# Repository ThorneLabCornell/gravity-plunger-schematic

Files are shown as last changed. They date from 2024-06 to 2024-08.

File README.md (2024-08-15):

# gravity-plunger-schematic

Schematic created with Altium Designer

# BOM
| Item                                                      | Link                                                                                                                                                                                       | Quantity | Unit Price (USD) | Sub-Total (USD) |
| --------------------------------------------------------- | ------------------------------------------------------------------------------------------------------------------------------------------------------------------------------------------ | -------- | ---------------- | --------------- |
| Steel Support Rod 1"x3'                                   | [https://www.mcmaster.com/6061K65/](https://www.mcmaster.com/6061K65/)                                                                                                                     | 1        | 44.71            | 44.71           |
| Face Mount Shaft Collar 1"                                | [https://www.mcmaster.com/9677T2/](https://www.mcmaster.com/9677T2/)                                                                                                                       | 3        | 15.83            | 47.49           |
| Face Mount Shaft Collar 5/8"                              | [https://www.mcmaster.com/9677T23/](https://www.mcmaster.com/9677T23/)                                                                                                                     | 3        | 14.5             | 43.5            |
| Flange-Mounted Shaft Support 1"                           | [https://www.mcmaster.com/57745K23/](https://www.mcmaster.com/57745K23/)                                                                                                                   | 1        | 73.46            | 73.46           |
| Linear Bearing 5/8"                                       | [https://www.mcmaster.com/60595K74/](https://www.mcmaster.com/60595K74/)                                                                                                                   | 2        | 27.33            | 54.66           |
| External Retaining Ring 1 1/8"                            | [https://www.mcmaster.com/9968K25/](https://www.mcmaster.com/9968K25/)                                                                                                                     | 4        | 2.23             | 8.92            |
| Tight-Tolerance 2024 Aluminum Rod 5/8"x3'                 | [https://www.mcmaster.com/9061K17-9061K173/](https://www.mcmaster.com/9061K17-9061K173/)                                                                                                   | 1        | 64.99            | 64.99           |
| Multipurpose 6061 Aluminum, 3/16"x3'                      | [https://www.mcmaster.com/8974K21/](https://www.mcmaster.com/8974K21/)                                                                                                                     | 1        | 4.27             | 4.27            |
| 10-24 Thread Size, 1-1/2" Long, Fully Threaded (25 Units) | [https://www.mcmaster.com/90044A115/](https://www.mcmaster.com/90044A115/)                                                                                                                 | 1        | 12.36            | 12.36           |
| 1/4"-20 Thread Size, 3/4" Long Screws (50 Units)          | [https://www.mcmaster.com/91251A540/](https://www.mcmaster.com/91251A540/)                                                                                                                 | 1        | 11.38            | 11.38           |
| 10-24 Thread Size, 7/16" Long Screws (25 Units)           | [https://www.mcmaster.com/91864A090/](https://www.mcmaster.com/91864A090/)                                                                                                                 | 1        | 10.19            | 10.19           |
| M3 x 0.5 mm Thread, 16 mm Long Screws (100 Units)         | [https://www.mcmaster.com/92005A126/](https://www.mcmaster.com/92005A126/)                                                                                                                 | 1        | 4.73             | 4.73            |
| M3 x 0.5 mm Thread Nuts (100 Units)                       | [https://www.mcmaster.com/90592A085/](https://www.mcmaster.com/90592A085/)                                                                                                                 | 1        | 2.62             | 2.62            |
| Air Tool Lubricant                                        | [https://www.amazon.com/Super-Lube-12004-Lubricant-Translucent/dp/B00N77RY8O](https://www.amazon.com/Super-Lube-12004-Lubricant-Translucent/dp/B00N77RY8O)                                 | 1        | 6.72             | 6.72            |
| DS3218MG Servo                                            | [https://www.amazon.com/ANNIMOS-Digital-Waterproof-DS3218MG-Control/dp/B076CNKQX4](https://www.amazon.com/ANNIMOS-Digital-Waterproof-DS3218MG-Control/dp/B076CNKQX4)                       | 1        | 13.59            | 13.59           |
| Shock Absorber                                            | [https://www.amazon.com/Bansbach-Easylift-FPD-1030A2-CW-Absorbers-Dampers/dp/B01IWIO3K4](https://www.amazon.com/Bansbach-Easylift-FPD-1030A2-CW-Absorbers-Dampers/dp/B01IWIO3K4)           | 1        | 10.33            | 10.33           |
| Arduino Uno R3                                            | [https://www.amazon.com/Arduino-A000066-ARDUINO-UNO-R3/dp/B008GRTSV6](https://www.amazon.com/Arduino-A000066-ARDUINO-UNO-R3/dp/B008GRTSV6)                                                 | 1        | 29               | 29              |
| Liquid Crystal LCD Screen                                 | [https://www.amazon.com/GeeekPi-Character-Backlight-Raspberry-Electrical/dp/B07S7PJYM6](https://www.amazon.com/GeeekPi-Character-Backlight-Raspberry-Electrical/dp/B07S7PJYM6)             | 1        | 10.99            | 10.99           |
| Electronic Grade Conformal Coating                        | [https://www.amazon.com/Clear-Electronic-Grade-Silicone-Squeeze/dp/B0063U2RT8](https://www.amazon.com/Clear-Electronic-Grade-Silicone-Squeeze/dp/B0063U2RT8)                               | 1        | 11.95            | 11.95           |
| M2M Jumper Wire Kit                                       | [https://www.amazon.com/Elegoo-EL-CP-004-Multicolored-Breadboard-arduino/dp/B01EV70C78](https://www.amazon.com/Elegoo-EL-CP-004-Multicolored-Breadboard-arduino/dp/B01EV70C78)             | 1        | 7                | 7               |
| Board Jumper Wire Kit                                     | [https://www.amazon.com/AUSTOR-Lengths-Assorted-Preformed-Breadboard/dp/B07CJYSL2T](https://www.amazon.com/AUSTOR-Lengths-Assorted-Preformed-Breadboard/dp/B07CJYSL2T)                     | 1        | 11.99            | 11.99           |
| Wire Connector Kit                                        | [https://www.amazon.com/Twidec-Connectors-Disconnect-Insulated-Assortment/dp/B09QWZ2V2G](https://www.amazon.com/Twidec-Connectors-Disconnect-Insulated-Assortment/dp/B09QWZ2V2G)           | 1        | 6.99             | 6.99            |
| Barrel Jack Connector                                     | [https://www.amazon.com/DZS-Elec-Connector-Experimental-5-5x2-1mm/dp/B07FDS11ZY](https://www.amazon.com/DZS-Elec-Connector-Experimental-5-5x2-1mm/dp/B07FDS11ZY)                           | 1        | 6.99             | 6.99            |
| Meter Stick                                               | https://www.amazon.com/Fisima-Large-Stainless-Measure-Straight/dp/B0C7Q3TKZH/                                                                                                              | 1        | 19.99            | 19.99           |
| 0.33uF Capacitor                                          | [https://www.digikey.com/en/products/detail/kemet/C412C334M5U5TA7200/818264](https://www.digikey.com/en/products/detail/kemet/C412C334M5U5TA7200/818264)                                   | 1        | 0.29             | 0.29            |
| 0.1uF Capacitor                                           | [https://www.digikey.com/en/products/detail/murata-electronics/RDER71H104K0K1H03B/4770969](https://www.digikey.com/en/products/detail/murata-electronics/RDER71H104K0K1H03B/4770969)       | 1        | 0.46             | 0.46            |
| 5V Voltage Regulator                                      | [https://www.digikey.com/en/products/detail/stmicroelectronics/L7805CV/585964](https://www.digikey.com/en/products/detail/stmicroelectronics/L7805CV/585964)                               | 1        | 0.58             | 0.58            |
| 12V Power Supply                                          | [https://www.digikey.com/en/products/detail/mean-well-usa-inc/RS-25-12/7706175](https://www.digikey.com/en/products/detail/mean-well-usa-inc/RS-25-12/7706175)                             | 1        | 11.93            | 11.93           |
| Circuit Protoboard                                        | [https://www.digikey.com/en/products/detail/sparkfun-electronics/PRT-12070/5230951](https://www.digikey.com/en/products/detail/sparkfun-electronics/PRT-12070/5230951)                     | 1        | 5.5              | 5.5             |
| 4 Pin Wire to Board Terminal                              | [https://www.digikey.com/en/products/detail/on-shore-technology-inc/OSTVN04A150/1588864](https://www.digikey.com/en/products/detail/on-shore-technology-inc/OSTVN04A150/1588864)           | 4        | 1.64             | 6.56            |
| 5 Pin Wire to Board Terminal                              | [https://www.digikey.com/en/products/detail/on-shore-technology-inc/OSTVN05A150/1588865](https://www.digikey.com/en/products/detail/on-shore-technology-inc/OSTVN05A150/1588865)           | 1        | 1.75             | 1.75            |
| 3 Pin Header                                              | [https://www.digikey.com/en/products/detail/samtec-inc/TS-103-G-A/1105459](https://www.digikey.com/en/products/detail/samtec-inc/TS-103-G-A/1105459)                                       | 1        | 1.19             | 1.19            |
| 200 Ohm Resistor                                          | [https://www.digikey.com/en/products/detail/stackpole-electronics-inc/CF14JT200R/1741336](https://www.digikey.com/en/products/detail/stackpole-electronics-inc/CF14JT200R/1741336)         | 2        | 0.1              | 0.2             |
| 10k Ohm Resistor                                          | [https://www.digikey.com/en/products/detail/stackpole-electronics-inc/CF14JT10K0/1741265](https://www.digikey.com/en/products/detail/stackpole-electronics-inc/CF14JT10K0/1741265)         | 3        | 0.1              | 0.3             |
| NO Push Button                                            | [https://www.digikey.com/en/products/detail/e-switch/PS1023ABLK/82862](https://www.digikey.com/en/products/detail/e-switch/PS1023ABLK/82862)                                               | 2        | 2.01             | 4.02            |
| Photoreflective Sensor                                    | [https://www.digikey.com/en/products/detail/tt-electronics-optek-technology/OPB704WZ/1637047](https://www.digikey.com/en/products/detail/tt-electronics-optek-technology/OPB704WZ/1637047) | 2        | 5.07             | 10.14           |
| 500mA Fuse                                                | [https://www.digikey.com/en/products/detail/eaton-electronics-division/BK-AGC-1-2-R/954156](https://www.digikey.com/en/products/detail/eaton-electronics-division/BK-AGC-1-2-R/954156)     | 1        | 0.83             | 0.83            |
| Fuse Holder Panel Mount                                   | [https://www.digikey.com/en/products/detail/littelfuse-inc/03453LF4HX040/16628034](https://www.digikey.com/en/products/detail/littelfuse-inc/03453LF4HX040/16628034)                       | 1        | 3.05             | 3.05            |
| Power Cord                                                | [https://www.digikey.com/en/products/detail/qualtek/311007-01/183390](https://www.digikey.com/en/products/detail/qualtek/311007-01/183390)                                                 | 1        | 3.37             | 3.37            |
| 20 AWG Red Wire 1'                                        | [https://www.digikey.com/en/products/detail/cnc-tech/1015-20-1-2000-004-1-TS/17799202](https://www.digikey.com/en/products/detail/cnc-tech/1015-20-1-2000-004-1-TS/17799202)               | 6        | 0.21             | 1.26            |
| 20 AWG Black Wire 1'                                      | [https://www.digikey.com/en/products/detail/cnc-tech/1015-20-1-2000-001-1-TS/17799212](https://www.digikey.com/en/products/detail/cnc-tech/1015-20-1-2000-001-1-TS/17799212)               | 6        | 0.204            | 1.22            |
| USB-A to USB-B M2M Wire                                   | [https://www.digikey.com/en/products/detail/assmann-wsw-components/AK672-2-2/947492](https://www.digikey.com/en/products/detail/assmann-wsw-components/AK672-2-2/947492)                   | 1        | 2.8              | 2.8             |

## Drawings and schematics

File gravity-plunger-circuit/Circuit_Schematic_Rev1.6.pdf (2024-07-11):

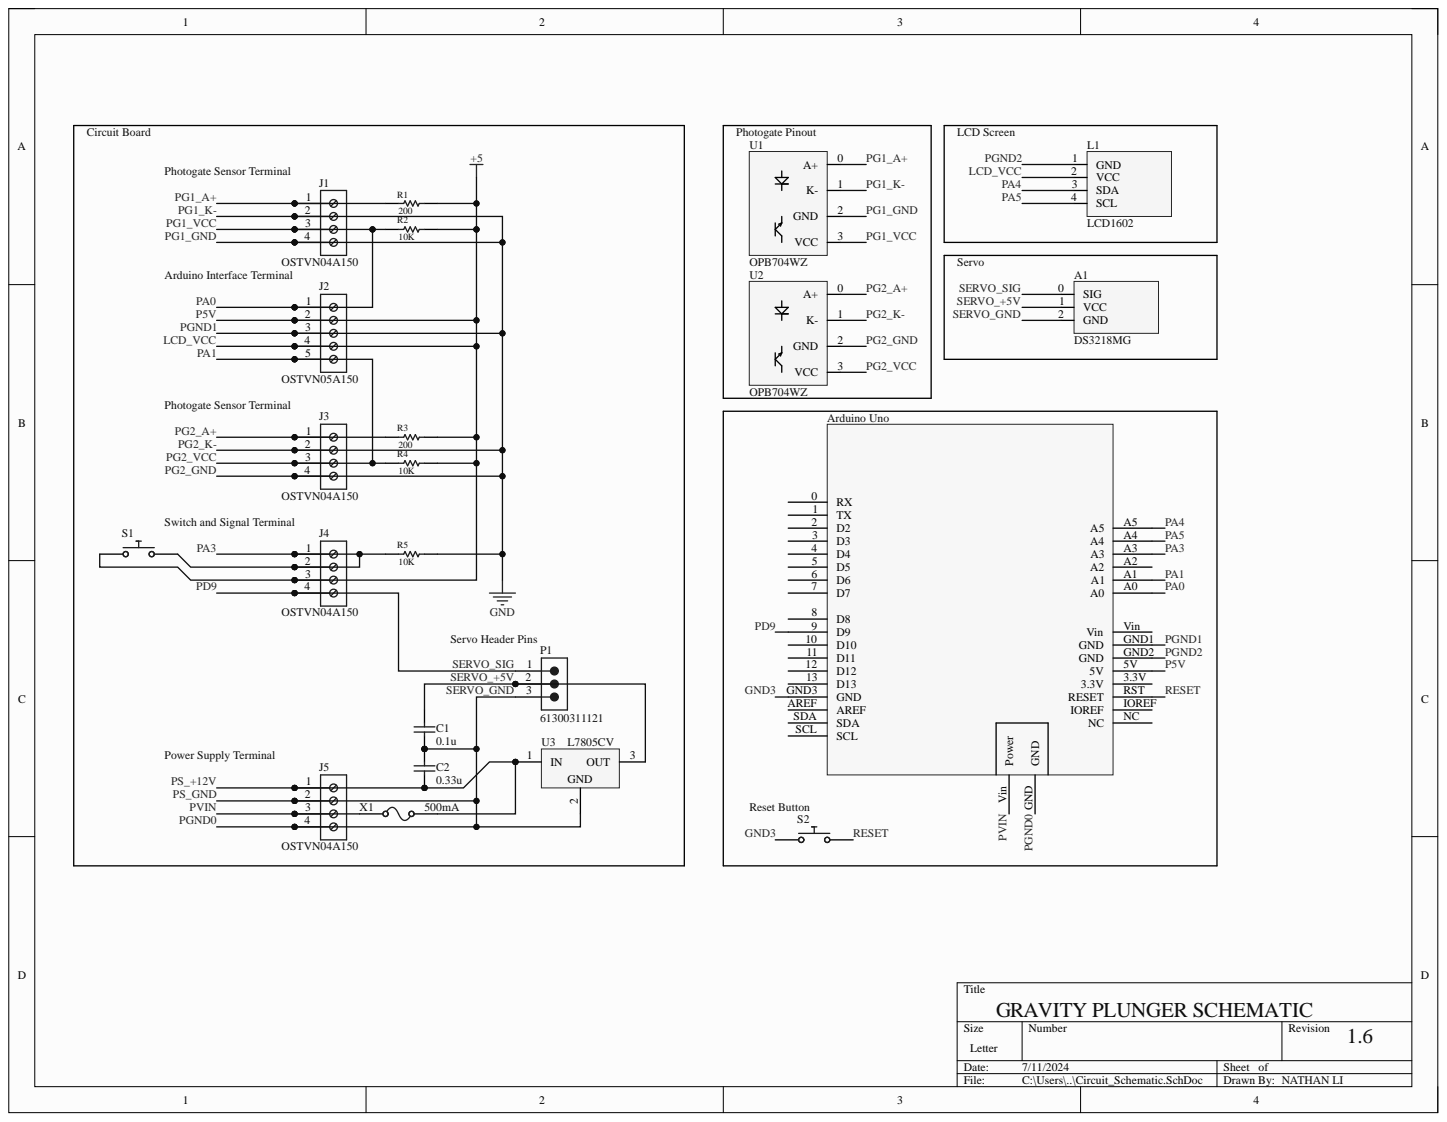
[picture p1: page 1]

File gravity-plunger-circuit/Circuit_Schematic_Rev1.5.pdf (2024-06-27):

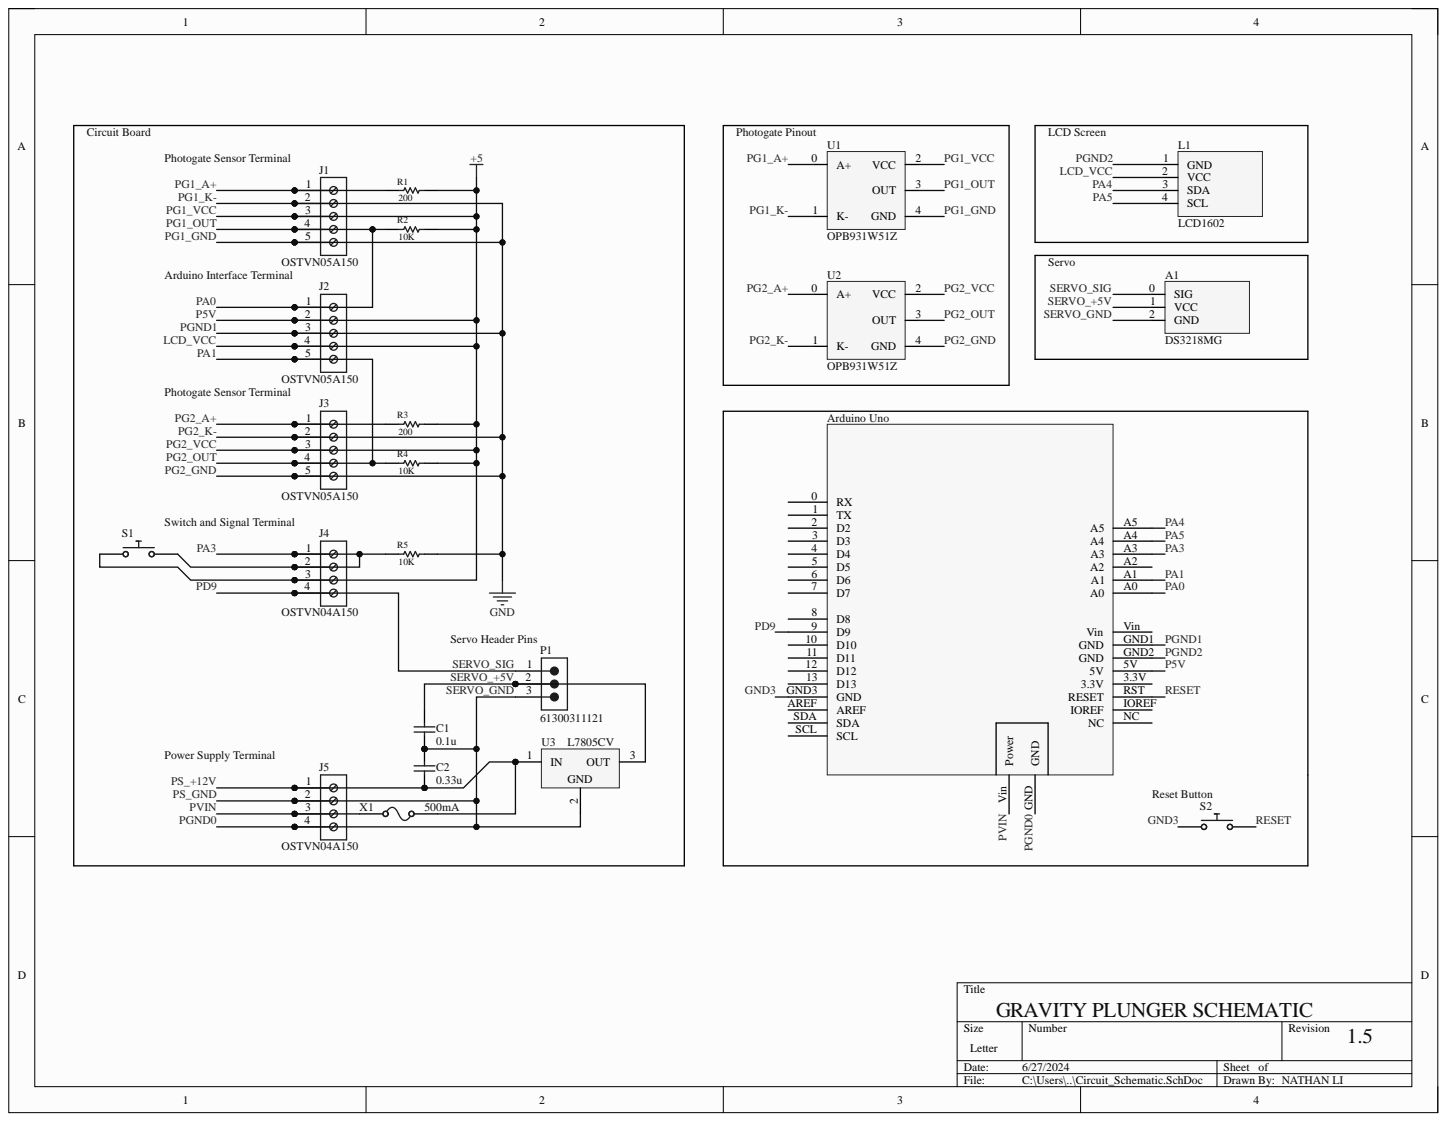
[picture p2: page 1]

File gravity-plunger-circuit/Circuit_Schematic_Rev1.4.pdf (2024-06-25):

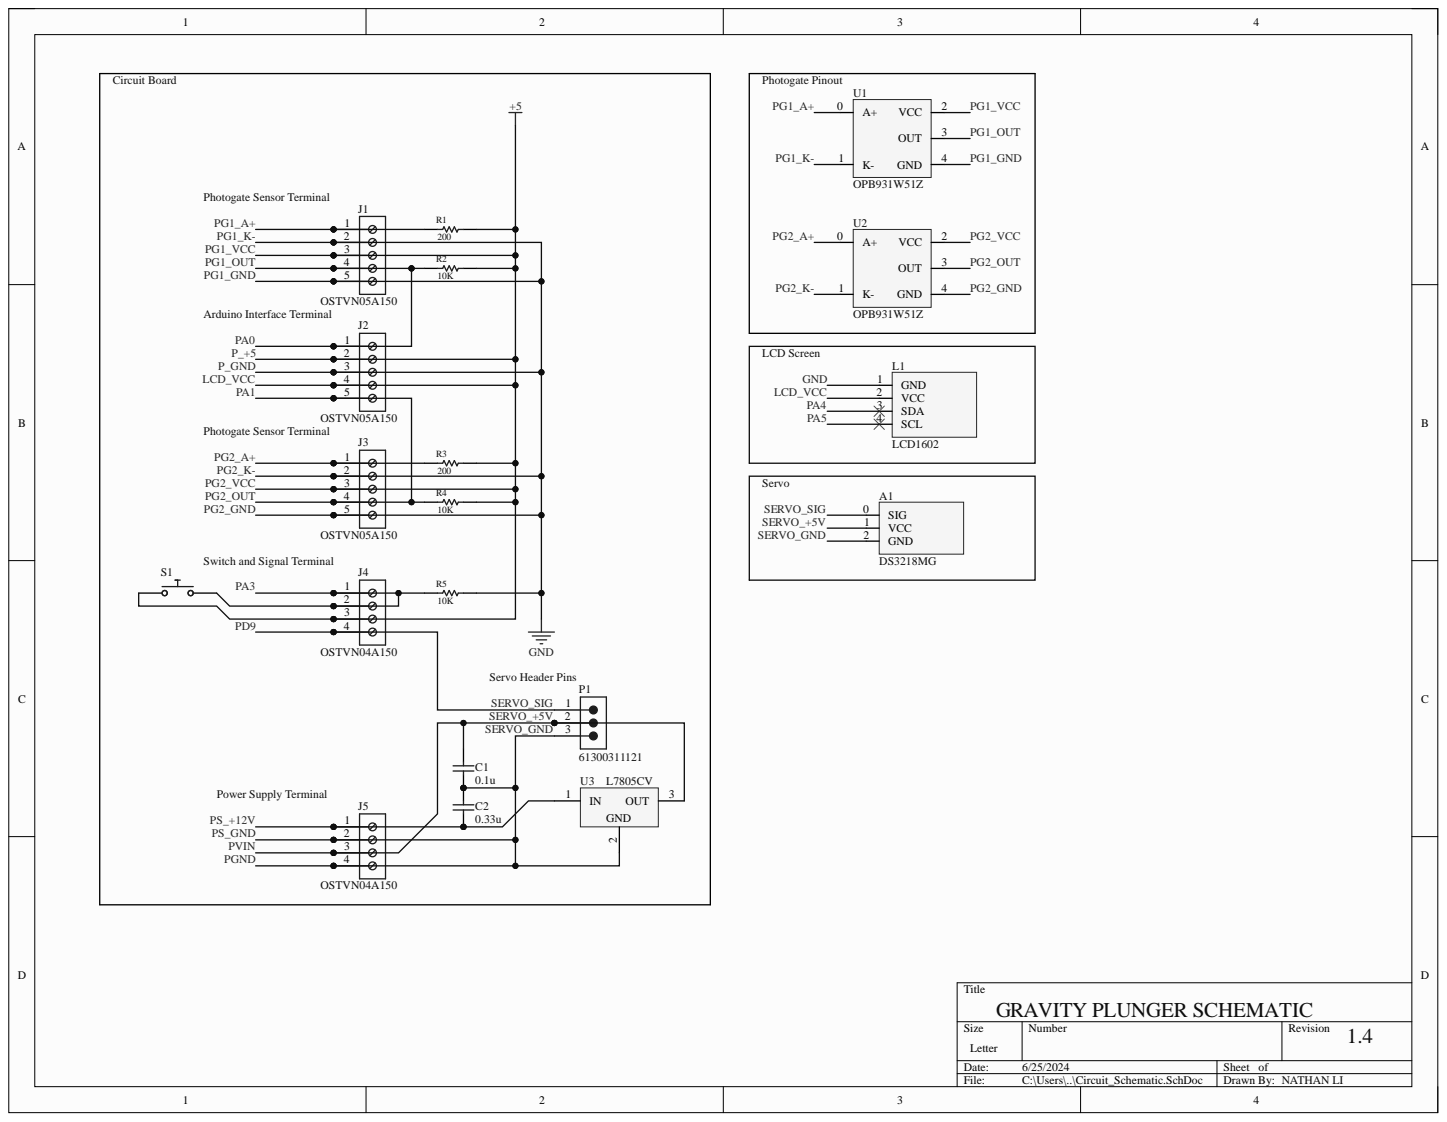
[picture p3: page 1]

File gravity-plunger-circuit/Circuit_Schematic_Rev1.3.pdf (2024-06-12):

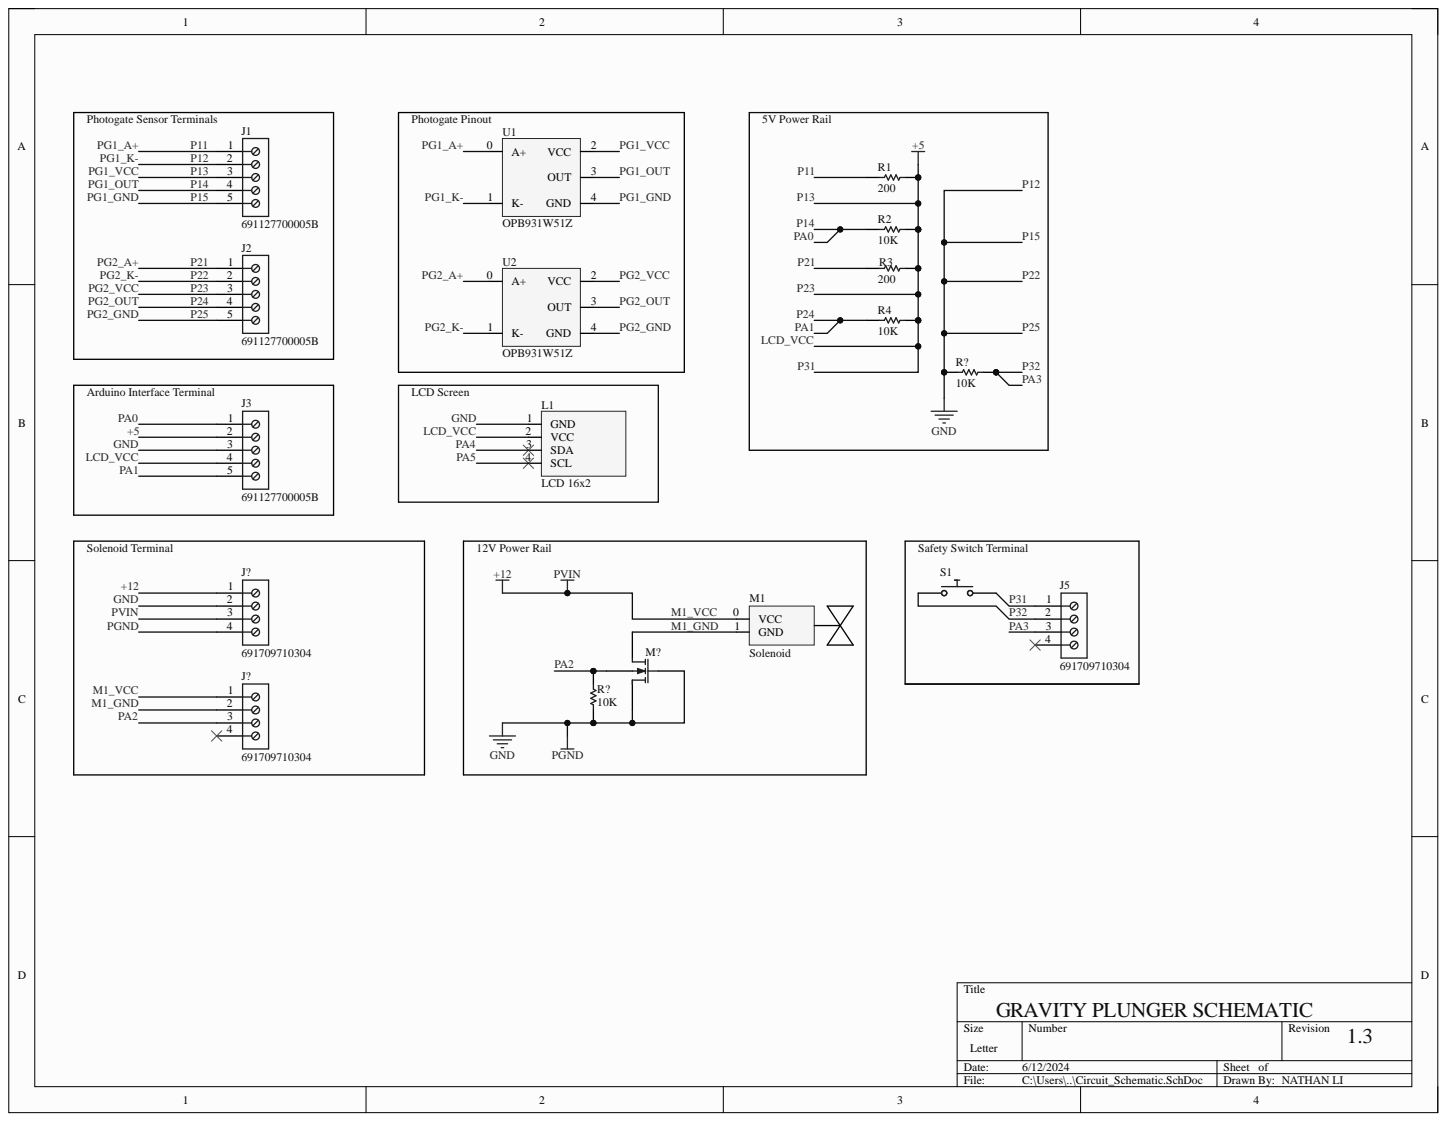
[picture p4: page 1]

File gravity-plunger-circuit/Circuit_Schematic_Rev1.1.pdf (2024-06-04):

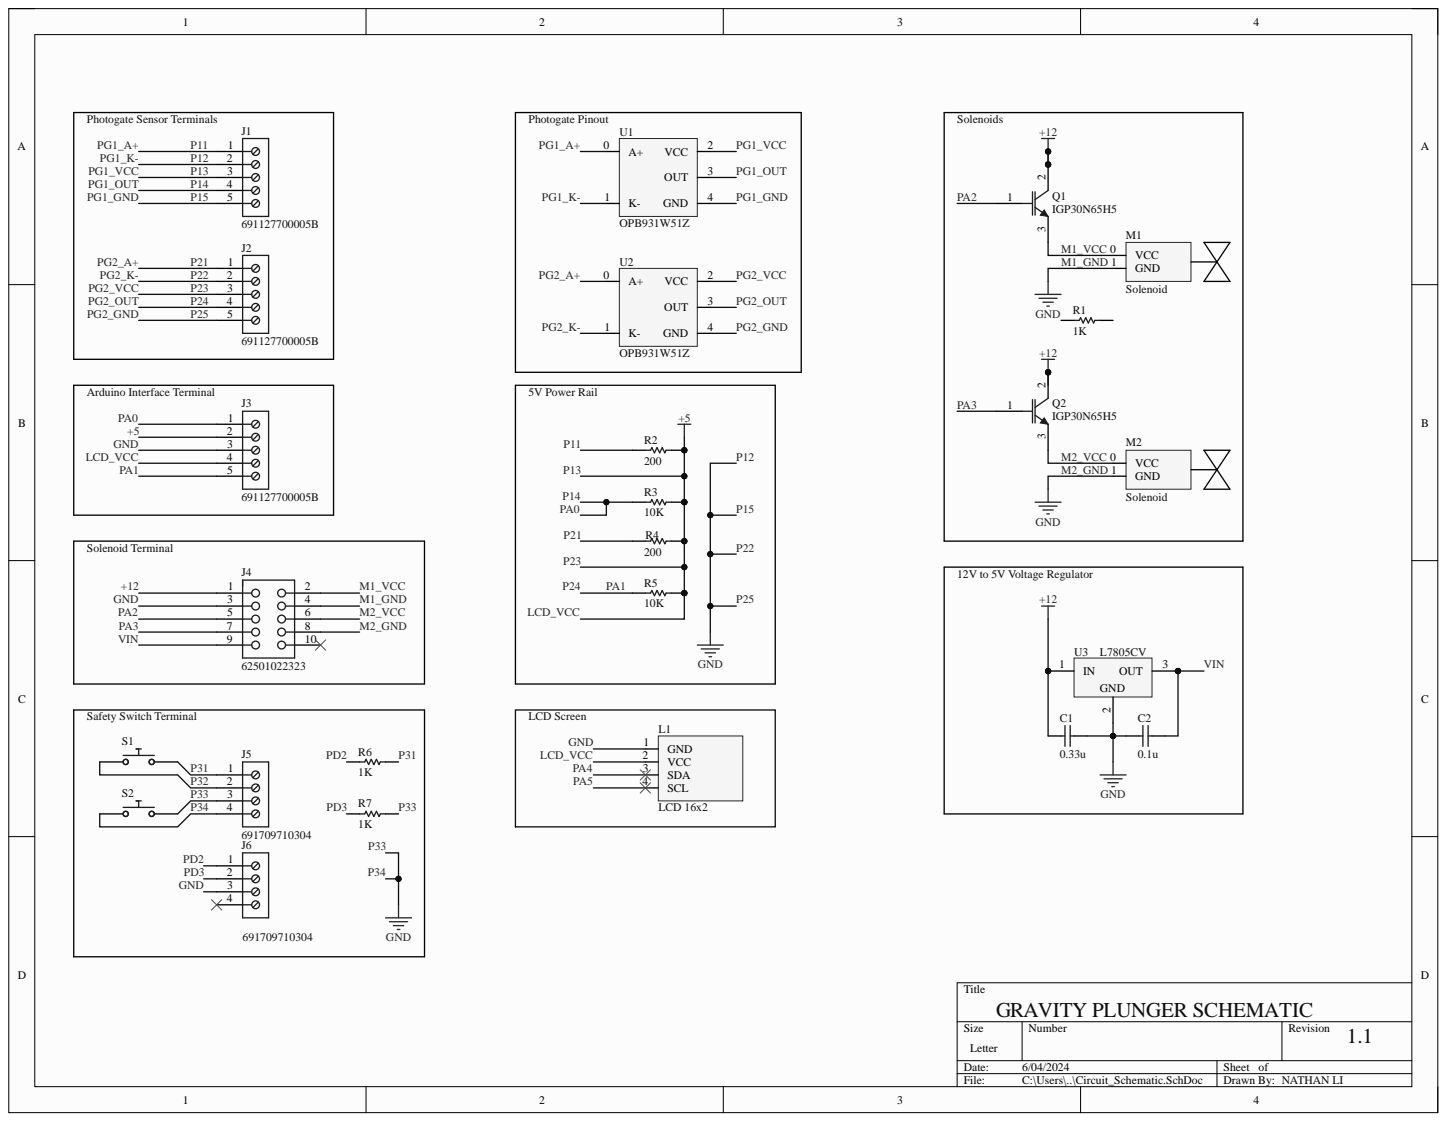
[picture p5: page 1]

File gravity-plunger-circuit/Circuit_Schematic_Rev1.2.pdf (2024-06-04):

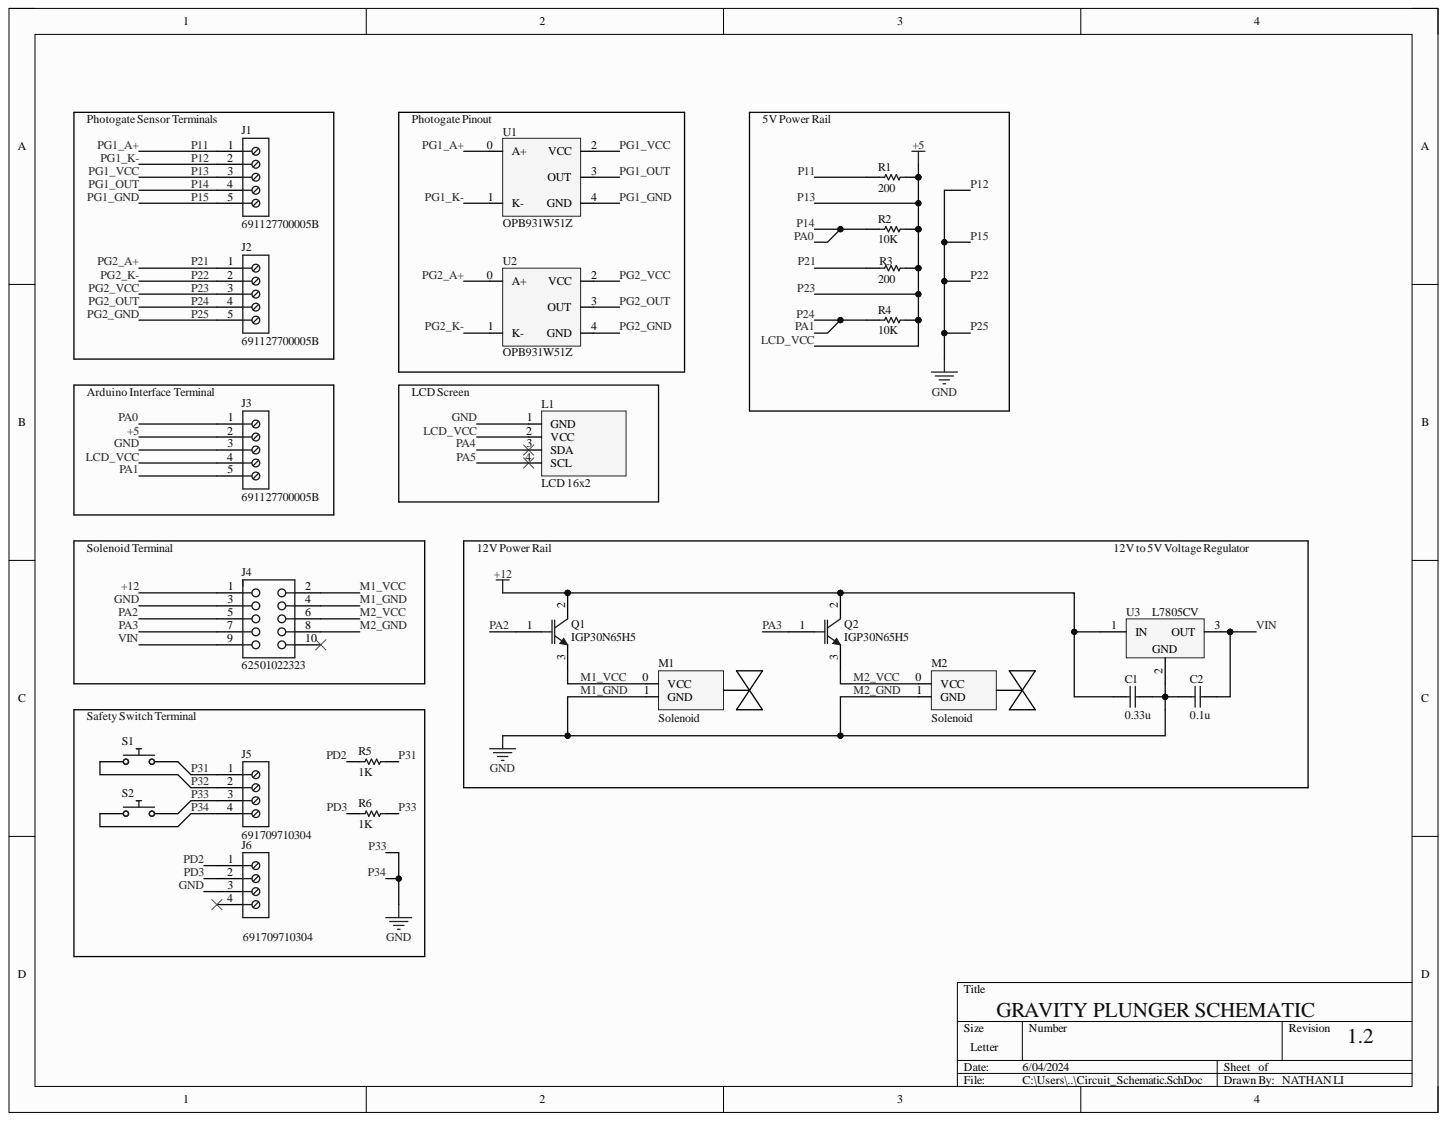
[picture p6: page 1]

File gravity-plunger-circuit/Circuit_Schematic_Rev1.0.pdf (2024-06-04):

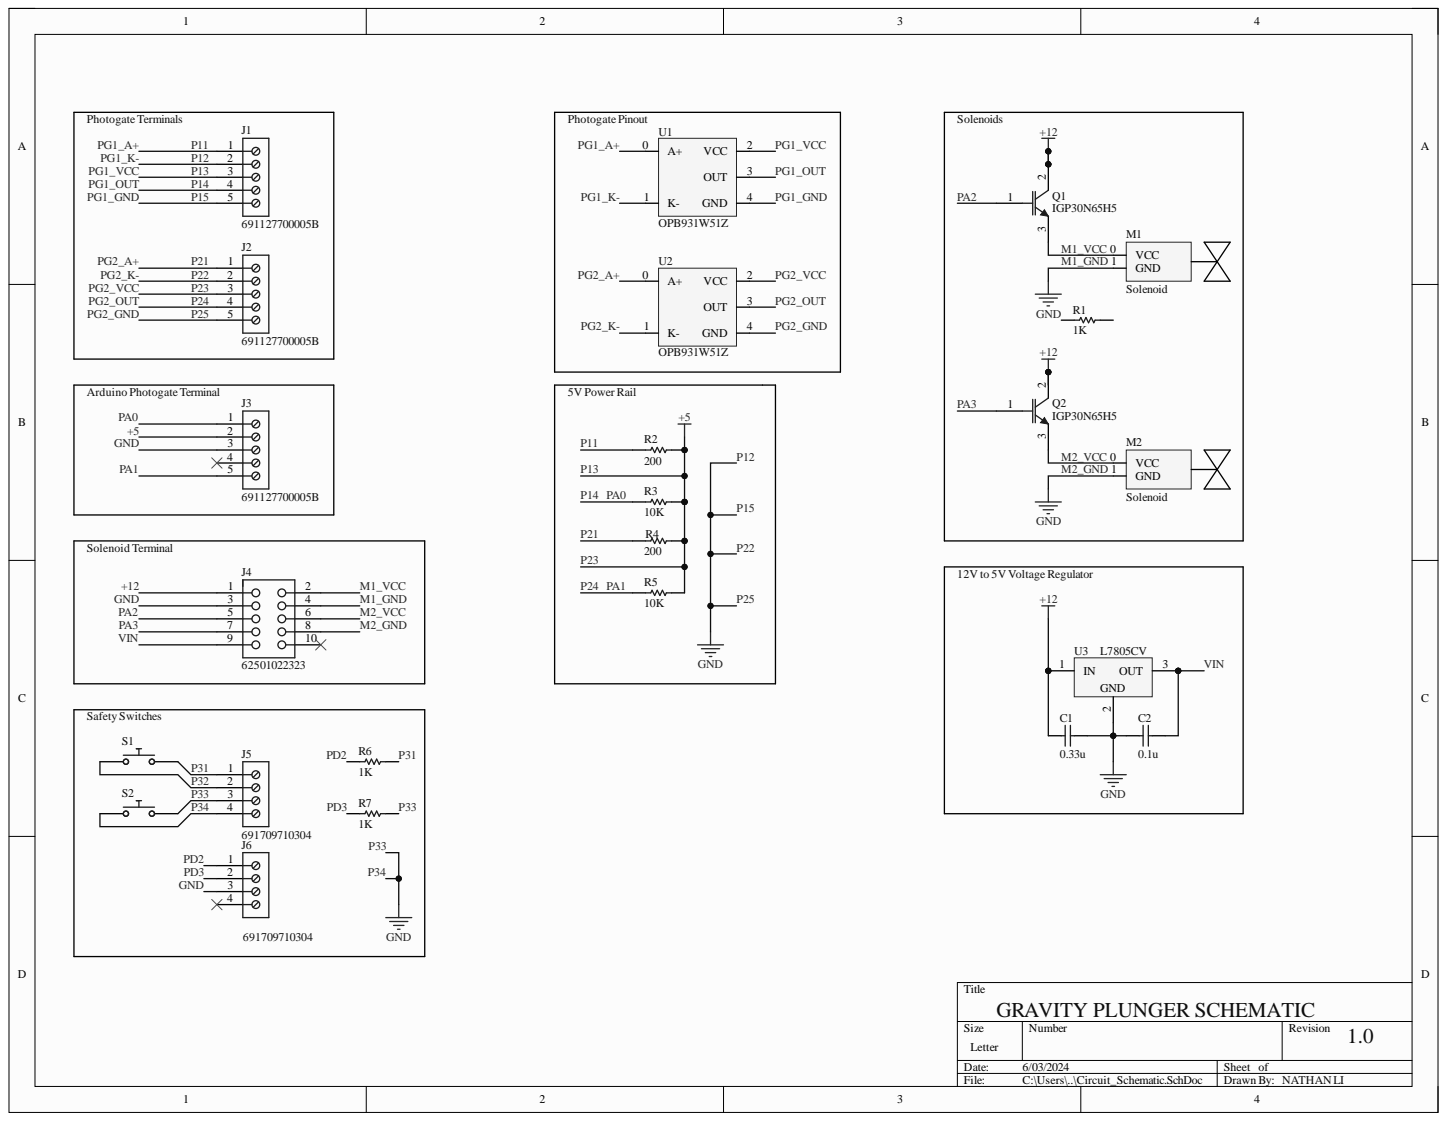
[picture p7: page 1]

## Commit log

2024-06-03 Added solenoid and voltage regulator schematics Created solenoid symbol Added terminal block schematics for photogates Added power rail schematics for photogates
    [Circuit_Schematic.SchDoc, SchemLib.SchLib, gravity-plunger-circuit.PrjPcb]
2024-06-03 + solenoid symbol + solenoid power schematic + 12V to 5V voltage regulator schematic + Net labels for photogate interrupters + Wire to board terminal schematics + Photogate power rail schematic
2024-06-03 Revision 1 + Switch and terminal schematic + Solenoid and +12V terminal schematic + Annotations and refactoring net labels
    [Circuit_Schematic.SchDoc]
2024-06-03 Added boxes and names to circuits
    [Circuit_Schematic.SchDoc]
2024-06-04 Rev 1.1 + LCD screen schematic
    [Circuit_Schematic.SchDoc, SchemLib.SchLib, gravity-plunger-circuit.PrjPcb]
2024-06-04 Rev 1.2 + Combined solenoid and VR circuits into 12V power rail circuit - Removed stray resistor R1
    [Circuit_Schematic.SchDoc]
2024-06-12 Rev 1.3 - 2->1 Solenoid - Voltage Regulator - 2->1 Safety switch + Modified mosfet schematic - 10 -> 4 pin terminal for solenoid
    [Circuit_Schematic.SchDoc]
2024-06-25 Rev 1.4 + Completed servo motor wiring + Replaced most net labels with wire connections + Modified servo schematic footprint to match physical wire order - Removed +12V power rail - Removed solenoid 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
    [Circuit_Schematic.SchDoc, SchemLib.SchLib]
2024-06-27 Rev 1.5 + Arduino schematic footprint + Reset switch + Fixed connection from Arduino Barrel Jack power from 5V->12V + Added 500mA fuse between 12V and Arduino power
    [Circuit_Schematic.SchDoc]
2024-07-11 Rev 1.6 + Added OPB704WZ photoelectric sensor footprint and implemented into circuit diagram + Replaced photogate 5 pin terminals -> 4 pin terminals for photoelectric sensors - Removed OPB931W51Z pho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
    [Circuit_Schematic.SchDoc, SchemLib.SchLib]
